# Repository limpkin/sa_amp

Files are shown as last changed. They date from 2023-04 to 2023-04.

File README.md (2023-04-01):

# sa_amp
A low noise DC to 600kHz amplifier

<p align="center">
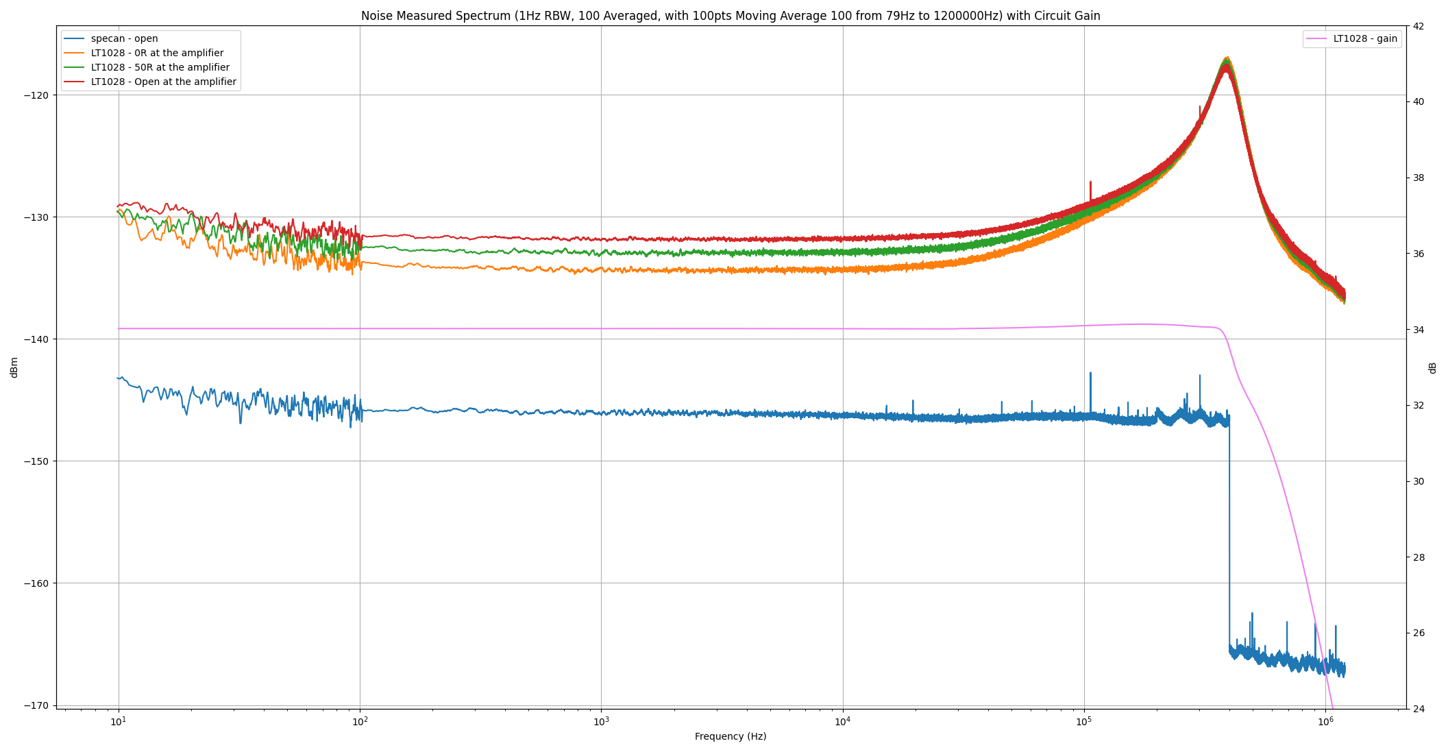
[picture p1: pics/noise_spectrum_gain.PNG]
Mooltipass Mini BLE
  
</p>

Main Specifications
- 0mV output offset voltage  
- 22dBm maximum output level  
- typical 0.9nV/sq(Hz) noise floor  
- 34dB gain between DC and 375kHz (.1dB)  
- 34dB gain between DC and 600kHz (3dB)  
- clipper activation artifact: 800ns 4V pulse (see here)

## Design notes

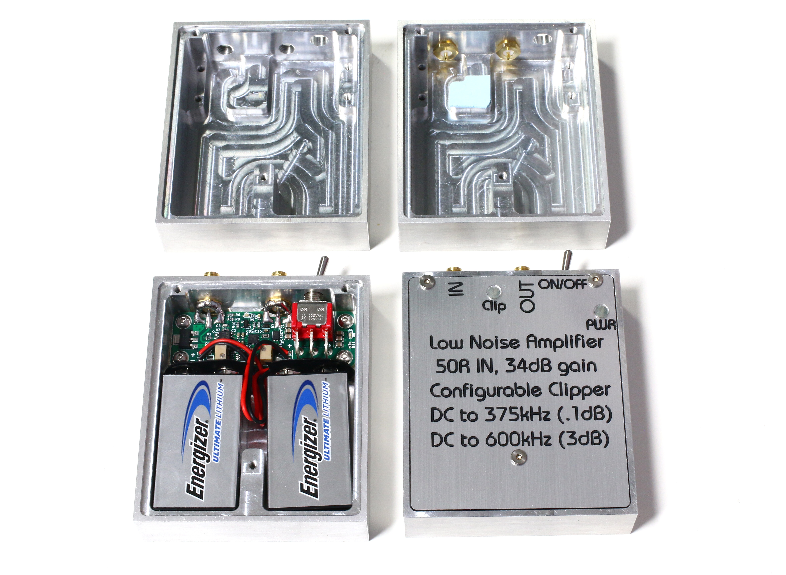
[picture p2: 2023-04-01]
pics/sa_amp_case.JPG

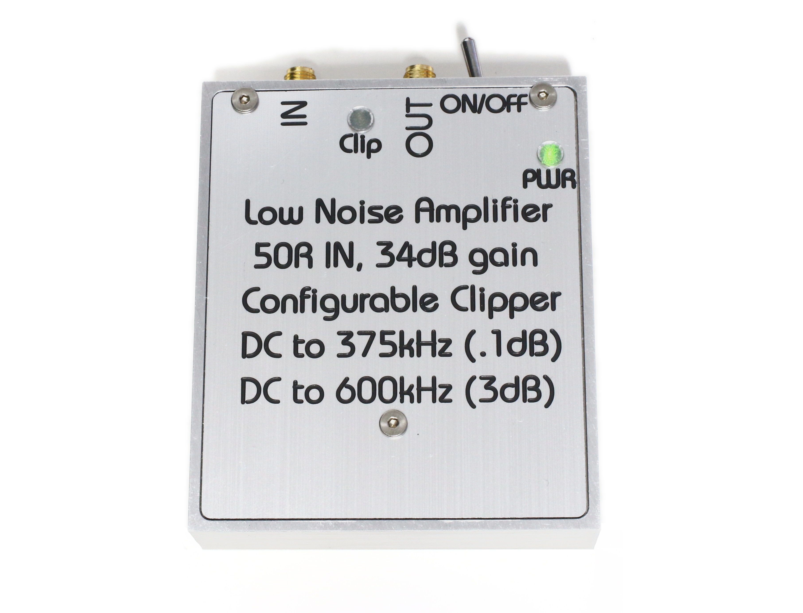
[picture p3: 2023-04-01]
pics/sa_amp_front.JPG

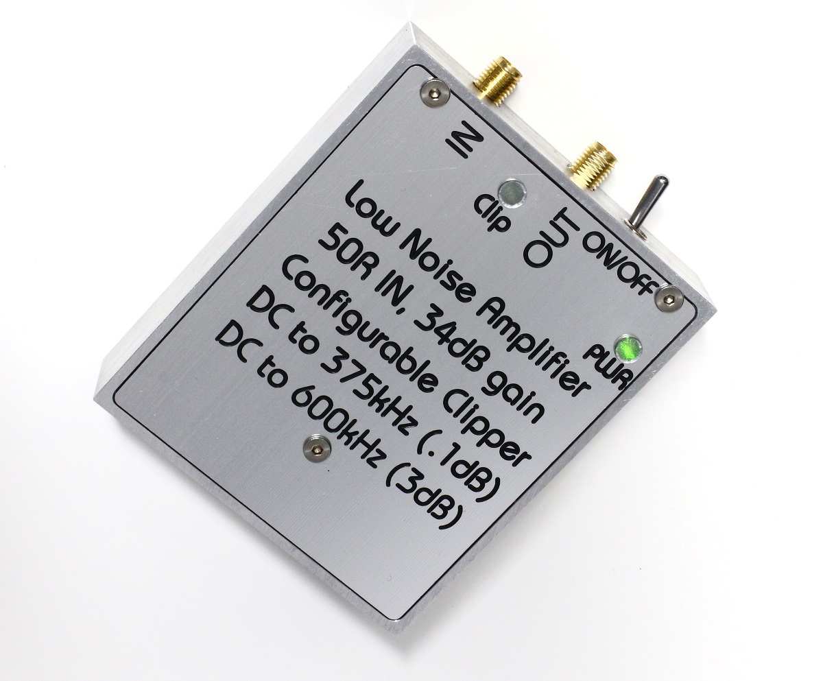
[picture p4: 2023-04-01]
pics/sa_amp_angle_1200.JPG

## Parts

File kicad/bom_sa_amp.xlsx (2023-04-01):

Item | References | Qty | Description | Manufacturer P/N | Manufacturer | Package | Internet Link | Supplier PN | Home ID | Home Stock | Supplier Stock | Part Status | Project Name
1 | C1, C3, C7, C9, C13, C16, | 6 | CAP CER 10UF 16V X5R 0805 | CL21A106KOQNNNE | Samsung Electro-Mechanics | 0805 (2012 Metric) | https://www.digikey.com/en/products/detail/samsung-electro-mechanics/CL21A106KOQNNNE/3886754 | 1276-1096-1-ND | ---- | 0 | 6,558,375 | Active | sa amp v3
2 | C2, C5, C6, C8, C10, C11, C12, C14, C15, C17, C18, | 11 | CAP CER 0.1UF 50V X7R 0603 | CL10B104KB8NNNC | Samsung Electro-Mechanics | 0603 (1608 Metric) | https://www.digikey.com/en/products/detail/samsung-electro-mechanics/CL10B104KB8NNNC/3886658 | 1276-1000-1-ND | ---- | 0 | 21,882,996 | Active | sa amp v3
3 | C4, | 1 | CAP CER 68PF 50V C0G/NP0 0603 | GCM1885C1H680JA16D | Murata Electronics | 0603 (1608 Metric) | https://www.digikey.com/en/products/detail/murata-electronics/GCM1885C1H680JA16D/1765209 | 490-4961-1-ND | ---- | 0 | 439,568 | Active | sa amp v3
4 | D2, | 1 | DIODE ARRAY SCHOTTKY 25V SOT223 | BAT120S,115 | Nexperia USA Inc. | SOT-223 | https://www.digikey.com/en/products/detail/nexperia-usa-inc/BAT120S-115/1232111 | 1727-5368-1-ND | ---- | 0 | 7,681 | Active | sa amp v3
5 | D3, | 1 | DIODE SCHOTTKY 40V 1A SOD323 | B5819WS-TP | Micro Commercial Co | SOD-323 | https://www.digikey.com/en/products/detail/micro-commercial-co/B5819WS-TP/2213555 | B5819WS-TPMSCT-ND | ---- | 0 | 2,923,285 | Active | sa amp v3
6 | Q1, | 1 | MOSFET N-CH 100V 1.9A TO236AB | PMV213SN,215 | Nexperia USA Inc. | TO-236AB | https://www.digikey.com/en/products/detail/nexperia-usa-inc/PMV213SN-215/1157786 | 1727-6294-1-ND | ---- | 0 | 359,893 | Active | sa amp v3
7 | U4, | 1 | IC SWITCH SPST 1OHM RON 8LFCSP | ADG1401BCPZ-REEL7 | Analog Devices Inc. | 8-LFCSP-WD (2x3) | https://www.digikey.com/en/products/detail/analog-devices-inc/ADG1401BCPZ-REEL7/2261062 | ADG1401BCPZ-REEL7CT-ND | ---- | 0 | 17,871 | Active | sa amp v3
8 | U1, | 1 | IC OPAMP GP 1 CIRCUIT 8SO | LT1028CS8#TRPBF | Analog Devices Inc. | 8-SO | https://www.digikey.com/en/products/detail/analog-devices-inc/LT1028CS8-TRPBF/959596 | LT1028CS8#TRPBFCT-ND | ---- | 0 | 0 | Active | sa amp v3
9 | U2, | 1 | IC AUDIO 2 CIRCUIT 10VSON | OPA1622IDRCR | Texas Instruments | 10-VSON (3x3) | https://www.digikey.com/en/products/detail/texas-instruments/OPA1622IDRCR/5804204 | 296-45038-1-ND | ---- | 0 | 16,009 | Active | sa amp v3
10 | U3, | 1 | IC VOLT COMPARATOR DUAL 8-TSSOP | LM293PT | STMicroelectronics | 8-TSSOP | https://www.digikey.com/en/products/detail/stmicroelectronics/LM293PT/1038688 | 497-7818-1-ND | ---- | 0 | 114,821 | Active | sa amp v3
11 | D1, | 1 | LED RED DIFFUSED 0603 SMD | SML-D12U8WT86 | Rohm Semiconductor | 1608 (0603) | https://www.digikey.com/en/products/detail/rohm-semiconductor/SML-D12U8WT86/1641799 | 511-1580-1-ND | ---- | 0 | 953,623 | Active | sa amp v3
12 | RV1, RV2, | 2 | TRIMMER 20K OHM 0.25W J LEAD TOP | 3214W-1-203E | Bourns Inc. |  | https://www.digikey.com/en/products/detail/bourns-inc/3214W-1-203E/248432 | 3214W-203ECT-ND | ---- | 0 | 10,309 | Active | sa amp v3
13 | R1, | 1 | RES 10 OHM 1% 1/10W 0603 | RC0603FR-0710RL | YAGEO | 0603 | https://www.digikey.com/en/products/detail/yageo/RC0603FR-0710RL/726879 | 311-10.0HRCT-ND | ---- | 0 | 4,601,351 | Active | sa amp v3
14 | R2, | 1 | RES 49.9 OHM 1% 1/10W 0603 | RC0603FR-0749R9L | YAGEO | 0603 | https://www.digikey.com/en/products/detail/yageo/RC0603FR-0749R9L/727264 | 311-49.9HRCT-ND | ---- | 0 | 4,272,192 | Active | sa amp v3
15 | R3, | 1 | RES 1K OHM 1% 1/10W 0603 | RC0603FR-071KL | YAGEO | 0603 | https://www.digikey.com/en/products/detail/yageo/RC0603FR-071KL/726843 | 311-1.00KHRCT-ND | ---- | 0 | 15,621,723 | Active | sa amp v3
16 | R4, R5, | 2 | RES SMD 100 OHM 1% 1/2W 0805 | ERJ-P06F1000V | Panasonic Electronic Components | 0805 | https://www.digikey.com/en/products/detail/panasonic-electronic-components/ERJ-P06F1000V/3982698 | P16057CT-ND | ---- | 0 | 742,685 | Active | sa amp v3
17 | R6, R8, R10, R11 | 4 | RES 10K OHM 1% 1/10W 0603 | RC0603FR-0710KL | YAGEO | 0603 | https://www.digikey.com/en/products/detail/yageo/RC0603FR-0710KL/726880 | 311-10.0KHRCT-ND | ---- | 0 | 49,595,428 | Active | sa amp v3
18 | R7, | 1 | RES 4.99K OHM 1% 1/10W 0603 | RC0603FR-074K99L | YAGEO | 0603 | https://www.digikey.com/en/products/detail/yageo/RC0603FR-074K99L/727219 | 311-4.99KHRCT-ND | ---- | 0 | 3,267,751 | Active | sa amp v3
19 | R9, | 1 | RES 2K OHM 1% 1/10W 0603 | RC0603FR-072KL | YAGEO | 0603 | https://www.digikey.com/en/products/detail/yageo/RC0603FR-072KL/727009 | 311-2.00KHRCT-ND | ---- | 0 | 3,736,755 | Active | sa amp v3
20 | SW1, | 1 | SWITCH TOGGLE DPDT 5A 120V | 100DP1T1B1M6QE | E-Switch |  | https://www.digikey.com/en/products/detail/e-switch/100DP1T1B1M6QE/3777864 | 100DP1T1B1M6QE-ND | ---- | 0 | 172 | Active | sa amp v3
21 | D4, | 1 | LED GREEN DIFFUSED 0603 SMD | SML-D12P8WT86 | Rohm Semiconductor | 1608 (0603) | https://www.digikey.com/en/products/detail/rohm-semiconductor/SML-D12P8WT86/1641798 | 511-1579-2-ND | ---- | 0 | 953,623 | Active | sa amp v3

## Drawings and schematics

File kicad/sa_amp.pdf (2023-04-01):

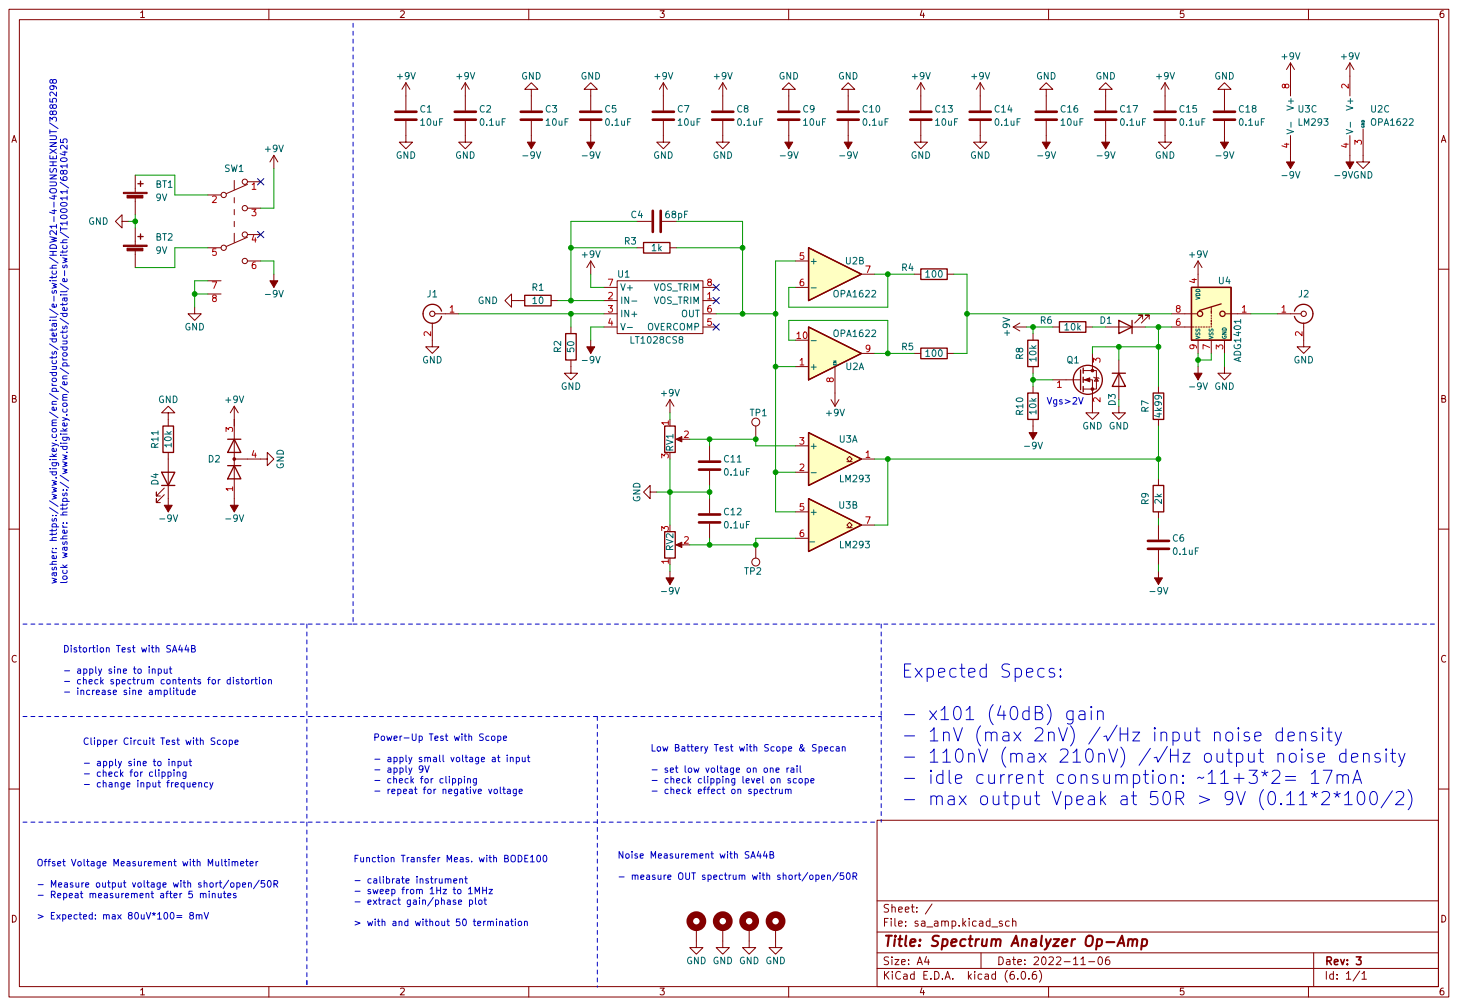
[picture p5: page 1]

- extract gain/phase plot > with and without 50 termination washer: https://www.digikey.com/en/products/detail/e-switch/HDW21-4-4OUNSHEXNUT/3885298 lock washer: https://www.digikey.com/en/products/detail/e-switch/T100011/6810425

- change input frequency Distortion Test with SA44B

- apply sine to input
- check spectrum contents for distortion
- increase sine amplitude

- x101 (40dB) gain
- idle current consumption: ~11+3*2= 17mA
- max output Vpeak at 50R > 9V (0.11*2*100/2)

Clipper Circuit Test with Scope

Power-Up Test with Scope

- apply small voltage at input
- apply 9V
- check for clipping
- repeat for negative voltage Function Transfer Meas. with BODE100

Low Battery Test with Scope & Specan

- set low voltage on one rail
- check clipping level on scope
- check effect on spectrum

Offset Voltage Measurement with Multimeter

- measure OUT spectrum with short/open/50R

- Measure output voltage with short/open/50R
- Repeat measurement after 5 minutes

- calibrate instrument - sweep from 1Hz to 1MHz

File: sa_amp.kicad_sch Sheet: /
Id: 1/1 Title: Spectrum Analyzer Op-Amp

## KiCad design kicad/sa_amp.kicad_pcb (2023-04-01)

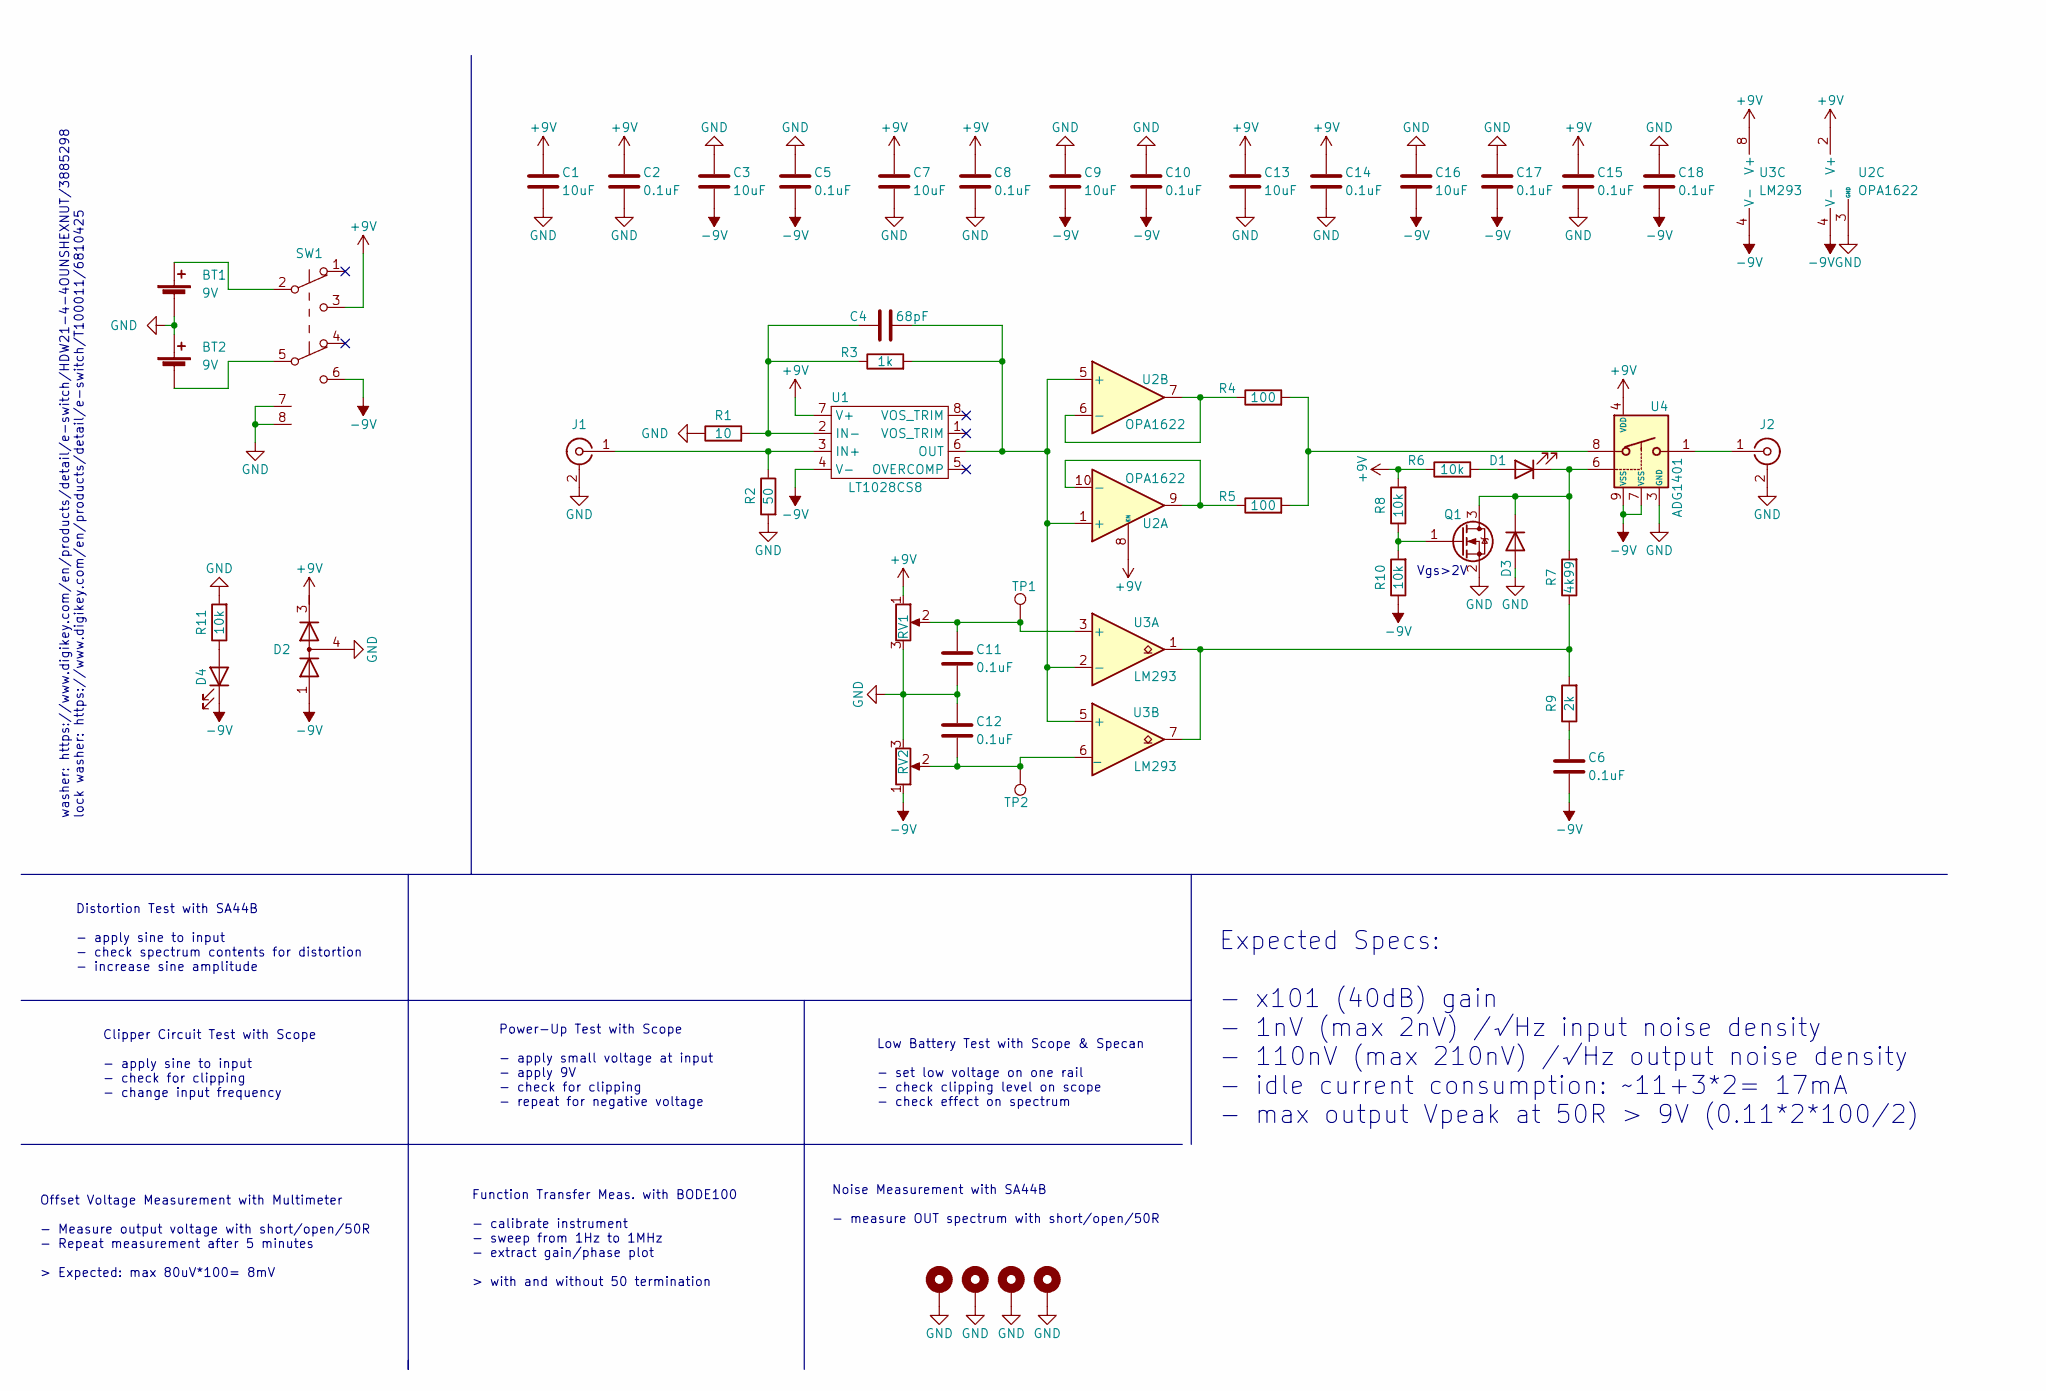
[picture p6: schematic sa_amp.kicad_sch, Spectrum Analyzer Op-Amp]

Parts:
BT1, BT2: 9V; PinSocket_2x01_P2.00mm_Vertical
C1, C3, C7, C9, C13, C16: 10uF; C_0805_2012Metric
C2, C5, C6, C8, C10, C11, C12, C14, C15, C17, C18: 0.1uF; C_0603_1608Metric
C4: 68pF; C_0603_1608Metric
D1, D4: LED; LED_0603_1608Metric
D2: D_Dual_Series_bat120s; SOT-223
D3: D; D_SOD-323
H1, H2, H3, H4: MountingHole_Pad; MountingHole_2.7mm_M2.5_Pad_TopOnly
J1, J2: Conn_Coaxial; 132139_LP
Q1: Q_NMOS_GSD; SOT-23
R1: 10; R_0603_1608Metric
R2: 50; R_0603_1608Metric
R3: 1k; R_0603_1608Metric
R4, R5: 100; R_0805_2012Metric
R6, R8, R10, R11: 10k; R_0603_1608Metric
R7: 4k99; R_0603_1608Metric
R9: 2k; R_0603_1608Metric
RV1, RV2: R_Potentiometer; Potentiometer_Bourns_3214W_Vertical
SW1: SW_Push_DPDT_100DP1T1B1M6QE; 100DP1T1B1M6QE
TP1, TP2: TestPoint; TestPoint_Pad_2.0x2.0mm
U1: LT1028CS8; SO-8_3.9x4.9mm_P1.27mm
U2: OPA1622; Texas_S-PVSON-N10
U3: LM293; TSSOP-8_4.4x3mm_P0.65mm
U4: ADG1401; WDFN-8-1EP_3x2mm_P0.5mm_EP1.65x1.8mm

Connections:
+9V: C1.1, C2.1, C7.1, C8.1, C13.1, C14.1, C15.1, D2.3 (K), R6.1, R8.2, RV1.1, SW1.3 (C), U1.7 (V+), U2.2 (V+), U2.8 (EN), U3.8 (V+), U4.4 (VDD)
-9V: C3.2, C5.2, C6.2, C9.2, C10.2, C16.2, C17.2, C18.2, D2.1 (A), D4.1 (K), R10.1, RV2.1, SW1.6 (C), U1.4 (V-), U2.4 (V-), U2.11 (V-), U3.4 (V-), U4.7 (VSS), U4.9 (VSS)
GND: BT1.2 (-), BT2.1 (+), C1.2, C2.2, C3.1, C5.1, C7.2, C8.2, C9.1, C10.1, C11.2, C12.1, C13.2, C14.2, C15.2, C16.1, C17.1, C18.1, D2.4 (common), D3.2 (A), H1.1, H2.1, H3.1, H4.1, J1.2 (Ext), J2.2 (Ext), Q1.2 (S), R1.1, R2.2, R11.2, RV1.3, RV2.3, SW1.7 (SHLD), SW1.8 (SHLD), U2.3 (GND), U4.3 (GND)
unnamed: BT1.1 (+), SW1.2 (B)
unnamed: BT2.2 (-), SW1.5 (B)
unnamed: C4.1, R1.2, R3.1, U1.2 (IN-)
unnamed: C4.2, R3.2, U1.6 (OUT), U2.1 (+), U2.5 (+), U3.2 (-), U3.5 (+)
unnamed: C6.1, R9.1
unnamed: C11.1, RV1.2, TP1.1, U3.3 (+)
unnamed: C12.2, RV2.2, TP2.1, U3.6 (_)
unnamed: D1.1 (K), D3.1 (K), Q1.3 (D), R7.2, U4.6
unnamed: D1.2 (A), R6.2
unnamed: D4.2 (A), R11.1
unnamed: J1.1 (In), R2.1, U1.3 (IN+)
unnamed: J2.1 (In), U4.1
unnamed: Q1.1 (G), R8.1, R10.2
unnamed: R4.1, U2.6 (-), U2.7
unnamed: R4.2, R5.2, U4.8
unnamed: R5.1, U2.9, U2.10 (-)
unnamed: R7.1, R9.2, U3.1, U3.7

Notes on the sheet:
Vgs>2V
Power-Up Test with Scope - apply small voltage at input - apply 9V - check for clipping - repeat for negative voltage
Low Battery Test with Scope & Specan - set low voltage on one rail - check clipping level on scope - check effect on spectrum
Clipper Circuit Test with Scope - apply sine to input - check for clipping - change input frequency
washer: https://www.digikey.com/en/products/detail/e-switch/HDW21-4-4OUNSHEXNUT/3885298 lock washer: https://www.digikey.com/en/products/detail/e-switch/T100011/6810425
Distortion Test with SA44B - apply sine to input - check spectrum contents for distortion - increase sine amplitude
Noise Measurement with SA44B - measure OUT spectrum with short/open/50R
Offset Voltage Measurement with Multimeter - Measure output voltage with short/open/50R - Repeat measurement after 5 minutes > Expected: max 80uV*100= 8mV
Expected Specs: - x101 (40dB) gain - 1nV (max 2nV) /√Hz input noise density - 110nV (max 210nV) /√Hz output noise density - idle current consumption: ~11+3*2= 17mA - max output Vpeak at 50R > 9V (0.11*2*100/2)
Function Transfer Meas. with BODE100 - calibrate instrument - sweep from 1Hz to 1MHz - extract gain/phase plot > with and without 50 termination

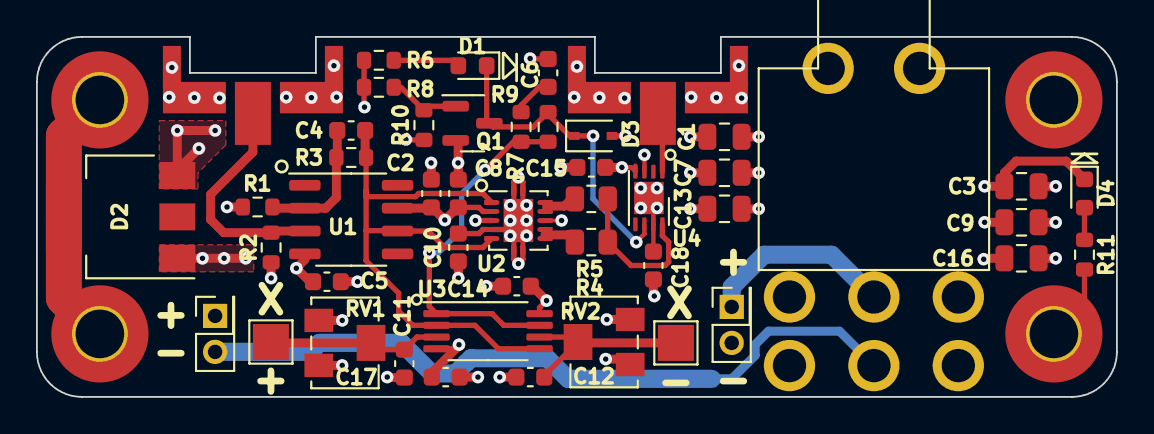
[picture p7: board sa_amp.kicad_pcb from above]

Board: 4 copper layers, 60.0 x 20.0 mm, 51 parts (0 on the bottom side), 20 nets.

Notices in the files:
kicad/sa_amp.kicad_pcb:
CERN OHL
